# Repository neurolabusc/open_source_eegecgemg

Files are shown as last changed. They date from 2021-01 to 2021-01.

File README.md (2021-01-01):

# DIY Electrophysiology

**Note: this is an old page in an active field. Please see the links at
the bottom of the page for projects that extend this work.** Electrodes
on the skin can be used to measure muscle (electromyography, EMG) brain
(electroencephalography, EEG) and heart (electrocardiogram, ECG/EKG)
activity. These electrophysiological measures are popular for clinical,
research and hobbyist applications (such as brain computer interfaces).
Most commercial systems are "medical grade" -- these expensive systems
offer high precision (16-24 bits), participant electrical isolation as
well as support. On the other hand, there are numerous "hobby grade"
solutions that are very inexpensive but do provide fewer features. Here
we describe a "research grade" solution offering the same precision and
safety of the medical systems, with the ability to add time stamps (for
averaging data across trials) at a much lower cost (though without the
FDA approval or support, so use these designs at your own risk).

## Overview

This is an open source project for recording high quality
electrophysiological data using an ADS129n compatible front-end. These
chips support 4 (ADS1294), 6 (ADS1296) and 8 (ADS1298, ADS1299) channels
for measurement with 24-bit precision (and if you need even more
channels, you can daisy-chain multiple chips). The ADS communicates
using a serial peripheral interface (SPI) link. In this design, an
Arduino-compatible microcontroller translates between SPI and a
Bluetooth or USB Serial Port Connection. Software in the Matlab and
Processing languages allows a computer to record these serial port
signals. The connection between the computer and the Arduino should be
electrically isolated -- either via a wireless bluetooth module (the
JY-MCU sells for \$8) or an electrically isolated USB connection (e.g.
using an ADUM4160, \$11).

One nice feature of the ADS129n is that they provide 24-bit precision.
This allows a single hardware design to be used for very different
applications (spanning EEG to ECG and EMG). In contrast, a 16-bit design
needs to be tuned for the small and slow signals of scalp recorded EEG
or the quick and relatively huge signals generated by superficial
muscles in EMG. The chip also contains a number of sophisticated options
for filtering data and acquiring ECG. The newer ADS1299 is
pin-compatible with the ADS1298 providing a bit better precision but
requiring more current.

The host computer can send signals to control the amplifier (e.g.
specify the number of channels to send, the amplifier gain, sample rate,
etc). The software and datasheets describe how to do this. Once the
computer has specified the desired settings, a RDATAC (read data
continuously) causes the amplifier to begin streaming data back until a
SDATAC (stop continuous data) command is sent. In my code, the Arduino
converts serial port signals directly to SPI signals, so the host
software has complete control of the ads129n setup, and the code is
identical for SPI or serial port communication. However, my Arduino code
does alter the format for RDATAC data when transferring data from the
SPI to serial port. The reason for this is that the SPI interface has a
tremendous amount of bandwidth (e.g. the Teensy 3 can in theory support
21 Mbs), whereas Bluetooth connections are much more limited (e.g.
inexpensive Bluetooth modules max out at about .4 Mbs). For every
sample, the ADS129x SPI link will send 3+3\*n bytes of data per channel,
where n is 4 (ADS1294), 6 (ADS1296) and 8 (ADS1298, ADS1299). Therefore,
even when you record a single channel (3 bytes), the ADS1298 sends 27
bytes of data per sample. To conserve bandwidth, this project sends
1+3\*n where n is the number of ACTIVE channels. Therefore, if you set a
channel to be disabled ("input shorted") it will not require bandwidth.
The first sample transmitted via the serial port is the same header byte
reported by the SPI data format -- this includes a signature (to help
detect the first byte in each sample) and 4 bits that report the status
of the 4 GPIO (general purpose inputs/outputs) that allow you to record
time stamps. This sounds complicated, but the example Matlab and
Processing software demonstrate how to implement these communications.

## Implementation

I prefer to use a [Teensy 3.0
(T3)](https://www.pjrc.com/store/teensy3.html) for this application. It
is inexpensive, natively supports 3.3v signals, and can support high
speed (460800 bps in my experience) BlueTooth communications. The T3 has
a hardware SPI port (pins 10-13) and an additional hardware serial port
(pins 0 and 1) which can be used for a bluetooth module. The image shows
the connections. Pins 0 and 1 are connected to the Bluetooth module. Pin
4 is connected to the ADS "START". Pin 5 is connected to the ADS "DRDY"
(data ready). Pin 10 is connected to CS (Chip Select). Pin 10 (DOUT) is
connected to the ADS "DIN" (Data In) while Pin 11 (DIN) is connected to
the ADS "DOUT" (Data out). Pin 13 is connected to the ADS "CLK" (clock).
Optionally, connect pin 2 to PWDN (power down), pin 3 to RESET (reset)
and pin 6 to CLKSEL (clock source). To omit these connections, PWDN,
RESET and CLKSEL should in theory be pulled high (to 3.3v, DVDD), though
with the demonstration boards they float high so can be left
unconnected. Note you can always send the RESET command as an op-code
from software. The T3 will also supply power to ads129n front end board
-- you will want to provide 5v, 3.3v and 0v (ground) in addition to
linking the ads129n analog ground (AGND) to the T3 0v with a 0 Ohm 1/10
Watt resistor (which acts like a fuse to protect the participant). The
Due image below shows the location of these pins on the ads129n front
end boards. This code works with an Arduino Due as well, though in my
experience the BlueTooth modules are limited to around 115200 bps
speeds, so it is less well suited for wireless communication. However,
it is important to note that the upcoming [EEG
Mouse](https://github.com/OpenElectronicsLab/eeg-mouse) design will have
the same microprocessor as the Due, so software should be optimal for
that application. The essential wiring for connecting a Due to the
ads1298 or ads1299 front end kits is shown on the left. Note that this
figure shows the BOTTOM of the front end board (so that the header pins
are accessible) and the top of the Due (so its pins are also
accessible). The J4 jumper gets the 5v, 3.3v and 0v (ground) power. The
J3 jumper has the signal pins -- the required pins are pins are the SPI
clock (SCK), Data Out (DOUT), Data In (DIN), chip select (CS), Data
Ready (DRDY) and Start (START). Again, note that the Arduino and ads129n
cross their DIN/DOUT -- in the figure I use '->DIN' to show that this
Due (DOUT) pin connects to the ads129n DIN pin. You must also connect
the ground to of the Due to the analog ground of the ads129n -- this
should be done with a zero ohm 1/10 watt resistor (that acts as a fuse
for protecting the participant). The diagram also shows the pins for
connecting a blue tooth module (TX1, RX1) -- remember the bluetooth
module also requires power. Please note that for wired communications my
software assumes you will connect your Due to your computer's USB port
with the Due's fast "Native" port rather than the slow "Programmer" port
(the Due has two USB sockets). In theory, you could use other Arduino
compatible devices for connecting to the ads129n devices. However, the
Arduino would need to support SPI and would need to have a high speed
serial port (older designs like the Uno have very slow serial
connections). Two possible candidates are the Teensy 2.0 and Arduino
Leonardo. However, be warned that these devices use 5 volt signals that
may not work with and **could even damage the ads129n** (which can only
handle signals up to \~3.4 volts). Therefore, you would need to add
voltage dividers to each signal line. Therefore, the T3 and Due (that
natively operate at 3.3v) are simpler for this application, and
generally provide better performance.

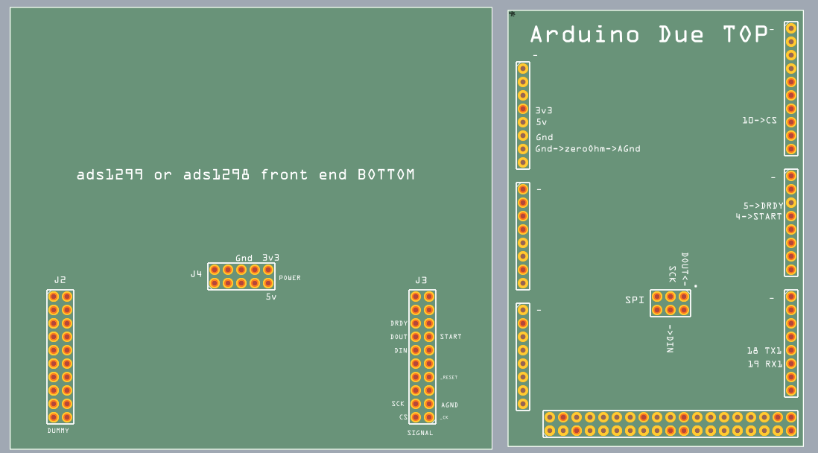
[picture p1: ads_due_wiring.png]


You can purchase the [ADS1298](https://www.ti.com/tool/ADS1298ECGFE-PDK)
(ideal for ECG) or [ADS1299](https://www.ti.com/tool/ads1299eegfe-pdk)
(ideal for EEG) Performance Demonstration Kits for about \$200. The
ADS1298 kit can connect to a standard EMG connector (about \$40). For
EMG or EEG you will probably be better served with the ADS1299 kit
connected to some DIN 42-802 sockets. In the near future expect to see a
less expensive, smaller open source design that can be used instead of
the demonstration kit (e.g. the [EEG Mouse
team's](https://github.com/OpenElectronicsLab/eeg-mouse) REV1 board will
integrate an Arduino compatible microcontroller on the same board as an
ADS1299, the previous REV0 design can be
[fabricated](https://oshpark.com/) and used instead of the demonstration
kit).

## Testing your wiring

The first program to run on your Arduino/T3 is the "adsArd_hello_world"
- this just makes sure that your Arduino is wired correctly to your
ads129n. Load this software onto your Arduino/T3 using a USB cable (make
sure to connect the cable to the 'Native' rather than 'Programmer' port
if you use a Due) and then select Tools/SerialMonitor. You should see a
message like "Device Type (ID Control Register): 62 Channels: 8"
repeated regularly. If this works, you have wired everything correctly.
If you are told the "Channels: 0" then there is a problem.

## Upgrading a Bluetooth Module

Most commercial Bluetooth modules are initially programmed to only
communicate at 9600bps. The included Arduino sketch
"Bluetooth_Programmer_Ard" allows you to reset your module for higher
speeds -- in my experience inexpensive modules run at 460800bps with the
Teensy 3 (and 115200 bps with the Due). You only have to run this script
once -- check the Arduino Serial Monitor to follow the progress. Once
your module is reprogrammed it will use the new speed whenever it is
restarted. Once you have reprogrammed your module, remember to put a
more useful sketch onto your Arduino (for example, the adsArd sketch
described below).

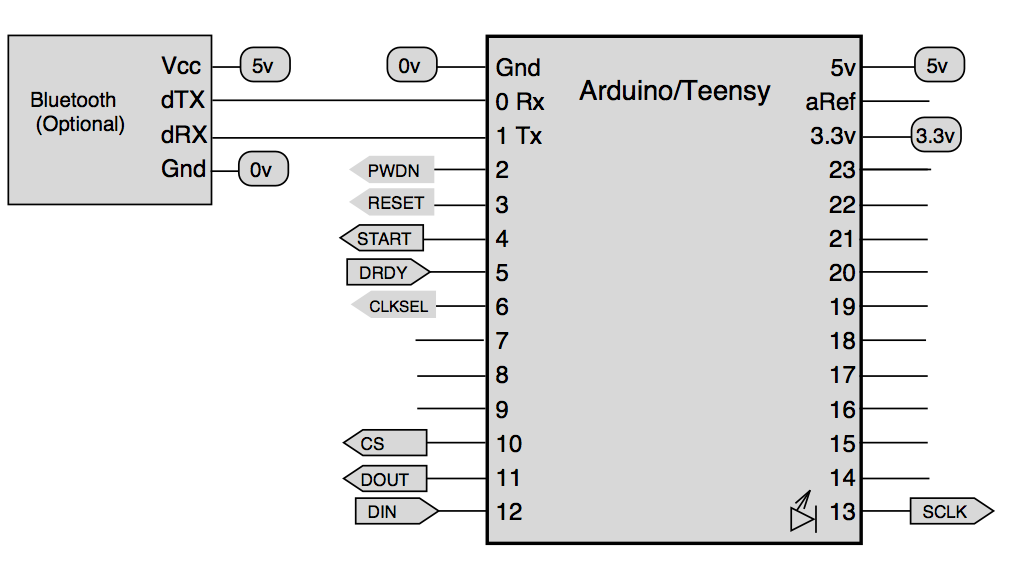
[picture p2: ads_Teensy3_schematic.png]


## Arduino Software

The Arduino sketch "adsArd" programs an Arduino-compatible device to
translate the ADS129n SPI data to the USB and BlueTooth ports. This
script has only been tested on the Teensy 3. We suspect it will work on
the Arduino Due once the developers tune the native serial port for
binary communications. Unless you use a Teensy3, you will need to edit a
few lines in adsCMD to specify the pins used for SPI communication (for
example, the [Teensy 2 uses pins 1,2,3 for SPI
communications](https://www.pjrc.com/teensy/td_libs_SPI.html) ). Once
your Arduino has been re-programmed, it will act as a SPI-serial
interposer whenever it is restarted. For the Teensy 3, the light on the
device will be off when the ADS129n is resting, dimly lit when the
ADS129n is streaming data, and will blink slowly if the Teensy is unable
to detect a ADS129x (check the connections between the Teensy and the
ADS129x).

## Matlab software

The Matlab software lets the user specify the sampling rate, number of
channels, and whether or not you wish to save the data. If requested,
the data will be saved in BrainVision analyzer format, which you can
view with the free ELEcro or EEGlab software.

## Processing software

By editing the first few lines of the Processing script you can specify
the sampling rate, number of channels, and whether or not you wish to
save the data. If requested, the data will be saved as tab-delimited
text. You can view these files with your favorite spreadsheet.

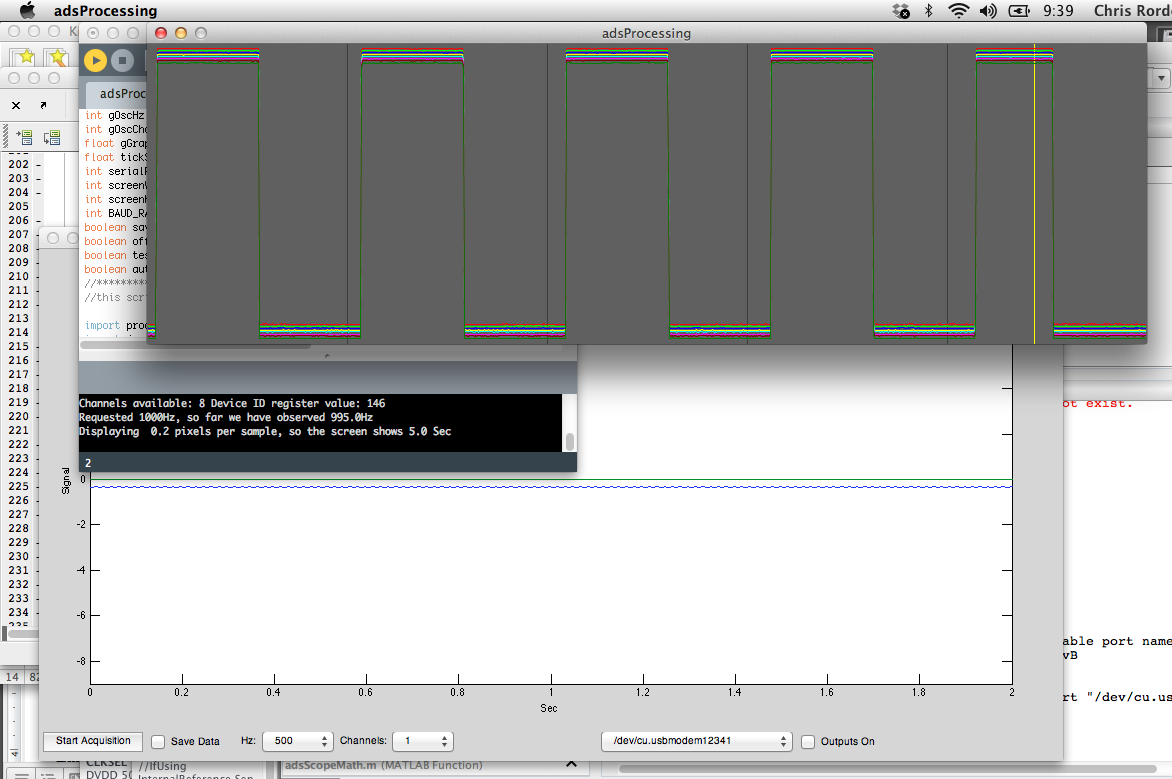
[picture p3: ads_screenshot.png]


## Links

 - [Chipstein](https://sites.google.com/site/chipstein/) describes probably the best hobby grade EMG (16-bit) and EEG (10-bit) around. The section on electrodes and skin preparation is vital for any electrophysiological recording.
 - The [EEG Mouse](https://github.com/OpenElectronicsLab/eeg-mouse) team are developing a complete open source ADS129n hardware project with an Arduino-compatible processor built onto the board. Our intention is that the software we describe on this page can be used on this hardware to record data.
 - The [ADS1298ECG Front End Performance Demonstration Kit](https://www.ti.com/tool/ADS1298ECGFE-PDK) includes a ADS1298 module that can be directly plugged into a Teensy 3 or other Arduino compatible device. Note that the configuration of the input channels is really optimized for ECG rather than EMG or EEG. The ads129n can do some sophisticated preprocessing of ECG data. EMG and EEG are simpler, but if you wish to use this demonstration kit for those applications you will need to use the jumpers appropriately.
 - [Raul Aguaviva](https://codinglab.blogspot.be/2013/07/my-heartbeat.html) describes a simple ECG system that can input into his [XOscillo](https://code.google.com/archive/p/xoscillo/) software.
 - [Scott Harden](https://www.swharden.com/blog/2013-04-14-simple-diy-ecg-pulse-oximeter-version-2/) describes the an elegantly simple hobby-grade ECG and optical pulse measurement system.
 - [Josh Wojnas](https://sites.google.com/site/openloopproject/Home/code-valt) provides plans for a simple ADS1298 hardware board.
 - StarCat provides the [HackEEG shield](https://starcat.io/products/hackeeg-shield/)
 - [OpenBCI](https://shop.openbci.com) provides impressive products.
 - The work described here has been extended by [Adam Feuer](https://github.com/adamfeuer/ADS129x-tools).

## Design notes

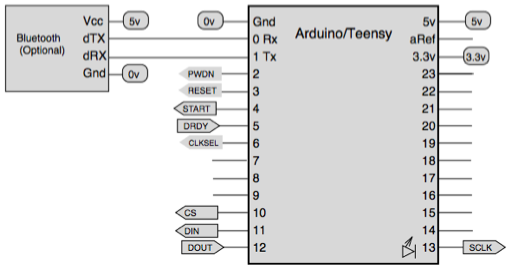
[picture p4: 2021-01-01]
source/teensy_wiring/ads_schematic.sketch/QuickLook/Thumbnail.png

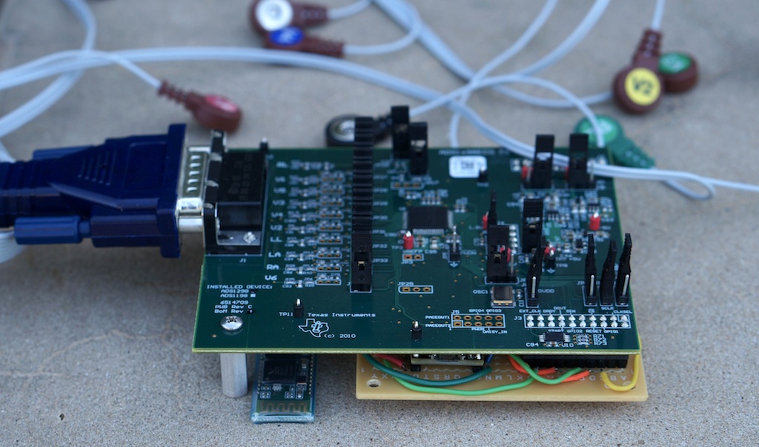
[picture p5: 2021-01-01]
photo_small.jpg

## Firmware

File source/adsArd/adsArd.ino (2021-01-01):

#define BAUD_RATE  460800 //specifies BlueTooth speed. top speeds appear to be around 115200 for Due, 460800 for Teensy3
#define txActiveChannelsOnly //reduce bandwidth: only send data for active data channels

#if defined(__SAM3X8E__)
  #define isDUE  //Detect Arduino Due
  #define WiredSerial SerialUSB //use Due's Native port
#else  
  #define WiredSerial Serial
#endif

#include "ads1298.h"
#include "adsCMD.h"
#include <SPI.h>  // include the SPI library:
int gMaxChan = 0;
int gNumActiveChan = 0;
int activeSerialPort = 0; //data will be sent to serial port that last sent commands. E.G. bluetooth or USB port
boolean gActiveChan [9]; // reports whether channels 1..9 are active
const int kPIN_LED = 13;//pin with light - typically 13. Only flashes if error status. n.b. on Teensy3, pin 13 is ALSO spi clock!
boolean isRDATAC = false;


void detectActiveChannels() {  //set device into RDATAC mode -it will stream data
  if ((isRDATAC) ||  (gMaxChan < 1)) return; //we can not read registers when in RDATAC mode
  using namespace ADS1298; 
  gNumActiveChan = 0;
  for (int i = 1; i <= gMaxChan; i++) {
    delayMicroseconds(1); 
     int chSet = adc_rreg(CHnSET + i);
     gActiveChan[i] = ((chSet & 7) != SHORTED);
     if ( (chSet & 7) != SHORTED) gNumActiveChan ++;   
  }
}

int Serialavailable(int serialNum) { //handle commands to ADS device
  switch (serialNum) {
    case 1:
      return Serial1.available() ;
    default: 
      return WiredSerial.available() ;
  }
}

int Serialread(int serialNum) { //handle commands to ADS device
  switch (serialNum) {
    case 1:
      return Serial1.read() ;
    default: 
      return WiredSerial.read() ;
  }
}

void checkSerialNum(int serialNum) { //handle commands to ADS device
  if (Serialavailable(serialNum) < 1) return;
  activeSerialPort = serialNum;
  unsigned char  val = Serialread(serialNum);      
  using namespace ADS1298; 
  if ((val >= 0x02) && (val <= 0x12)) { //single byte command
        if (val == RDATAC) {
          detectActiveChannels(); //start streaming data
          if (gNumActiveChan > 0) isRDATAC = true;
        }
        if (val == SDATAC) isRDATAC = false;
        if (val == RDATA) isRDATAC = false;
        adc_send_command(val);
        return;
  }
  if ((val >= 0x20) && (val <= 0x3F)) { //RREG (Read register) command  
      for (int i = 0; i < 10; ++i) if (Serialavailable(serialNum) < 1) delay(1); 
      if(Serialavailable(serialNum) < 1) return;
      unsigned char  numSerialBytes = Serialread(serialNum)+1;
      digitalWrite(IPIN_CS, LOW);
      SPI.transfer(val);
      SPI.transfer(numSerialBytes-1);	// number of registers to be read – 1
      unsigned char serialBytes[numSerialBytes];
      for (int i = 0; i < numSerialBytes; ++i) 
        serialBytes[i] =SPI.transfer(0);
      delayMicroseconds(1);     
      digitalWrite(IPIN_CS, HIGH);
      switch (serialNum) {
        case 1:
          Serial1.write(serialBytes, numSerialBytes);
          Serial1.flush();
          break;
        default: 
            WiredSerial.write(serialBytes, numSerialBytes);
            WiredSerial.flush();
      }
      return;
  }
  if ((val >= 0x40) && (val <= 0x5F)) { //WREG (Write Register) command
      for (int i = 0; i < 5; ++i) if (Serialavailable(serialNum) < 1) delay(1); 
      if(Serialavailable(serialNum) < 1) return;
      unsigned char  numSerialBytes = Serialread(serialNum)+1;
      for (int i = 0; i < 5; ++i) if (Serialavailable(serialNum) < numSerialBytes) delay(1); 
      if(Serialavailable(serialNum) < numSerialBytes) return;
      unsigned char serialBytes[numSerialBytes];
      for (int i = 0; i < numSerialBytes; ++i) serialBytes[i] = Serialread(serialNum); 
      digitalWrite(IPIN_CS, LOW);
      SPI.transfer(val);
      SPI.transfer(numSerialBytes-1);	// number of registers to be written – 1
      for (int i = 0; i < numSerialBytes; ++i) {
        SPI.transfer(serialBytes[i]);
        delayMicroseconds(1);      
      }
      digitalWrite(IPIN_CS, HIGH);
  }//if WREG
}

//#define testSignal //use this to determine if your software is accurately measuring full range 24-bit signed data -8388608..8388607
#ifdef testSignal
  int testInc = 1;
  int testPeriod = 100;
  byte testMSB, testLSB; 
#endif 

void sendOsc(void) { 
    if ((!isRDATAC) || (gNumActiveChan < 1) )  return;
    if (digitalRead(IPIN_DRDY) == HIGH) return; 
    digitalWrite(IPIN_CS, LOW);
    #ifdef txActiveChannelsOnly
      int numSerialBytes = 1 + (3 * gNumActiveChan); //8-bits header plus 24-bits per ACTIVE channel
      unsigned char serialBytes[numSerialBytes];
      int i = 0;
      serialBytes[i++] =SPI.transfer(0); //get 1st byte of header
      SPI.transfer(0); //skip 2nd byte of header
      SPI.transfer(0); //skip 3rd byte of header
      for (int ch = 1; ch <= gMaxChan; ch++) {
        if (gActiveChan[ch]) {
           #ifdef testSignal
            //positive full-scale input produces  7FFFFFh, negative full-scale input produces 800000h, neutroal produces 000000h 
            testInc++;
            if (testInc >= testPeriod) {
              testInc = 1;
              if (testMSB == 0x7F) { //send minimum value -8388608;
                testMSB = 0x80;
                testLSB = 0x00;
              } else if (testMSB == 0x80) { //send zero
                testMSB = 0x00;
                testLSB = 0x00;             
              } else { //send maximum value +8388607
                testMSB = 0x7F;
                testLSB = 0xFF;
              } 
            }
            serialBytes[i++] = testMSB;
            serialBytes[i++] = testLSB;
            serialBytes[i++] = testLSB;
            SPI.transfer(0); SPI.transfer(0); SPI.transfer(0);
          #else //if testSignal otherwise report real data
            serialBytes[i++] =SPI.transfer(0);
            serialBytes[i++] =SPI.transfer(0);
            serialBytes[i++] =SPI.transfer(0); 
          #endif
        } else {
          SPI.transfer(0); SPI.transfer(0); SPI.transfer(0); //skip these 24 bytes
        }  
      }
      //for (int i = 0; i < numSerialBytes; ++i) 
      //  serialBytes[i] =SPI.transfer(0);
    #else
      int numSerialBytes = (3 * (gMaxChan+1)); //24-bits header plus 24-bits per channel
      unsigned char serialBytes[numSerialBytes];
      for (int i = 0; i < numSerialBytes; ++i) 
        serialBytes[i] =SPI.transfer(0);
     #endif 
     delayMicroseconds(1); 
     digitalWrite(IPIN_CS, HIGH);
     switch (activeSerialPort) {
        case 1:
          Serial1.write(serialBytes, numSerialBytes);
          break;
        default: 
            WiredSerial.write(serialBytes, numSerialBytes);;
      }
}

void adsSetup() { //default settings for ADS1298 and compatible chips
        using namespace ADS1298;
        // All GPIO set to output 0x0000: (floating CMOS inputs can flicker on and off, creating noise)
	adc_wreg(GPIO, 0);
        adc_wreg(CONFIG3,PD_REFBUF | CONFIG3_const);
	//FOR RLD: Power up the internal reference and wait for it to settle
        // adc_wreg(CONFIG3, RLDREF_INT | PD_RLD | PD_REFBUF | VREF_4V | CONFIG3_const);
	// delay(150);
	// adc_wreg(RLD_SENSP, 0x01);	// only use channel IN1P and IN1N
	// adc_wreg(RLD_SENSN, 0x01);	// for the RLD Measurement
        adc_wreg(CONFIG1,HIGH_RES_1k_SPS);
        adc_wreg(CONFIG2, INT_TEST);	// generate internal test signals
	// Set the first two channels to input signal
	for (int i = 1; i <= 8; ++i) {
		adc_wreg(CHnSET + i, ELECTRODE_INPUT | GAIN_12X); //report this channel with x12 gain
		//adc_wreg(CHnSET + i, TEST_SIGNAL | GAIN_12X); //create square wave
                //adc_wreg(CHnSET + i,SHORTED); //disable this channel
	}
	digitalWrite(PIN_START, HIGH);  
}

void setup(){
  using namespace ADS1298;
  //prepare pins to be outputs or inputs
  //pinMode(PIN_SCLK, OUTPUT); //optional - SPI library will do this for us
  //pinMode(PIN_DIN, OUTPUT); //optional - SPI library will do this for us
  //pinMode(PIN_DOUT, INPUT); //optional - SPI library will do this for us
  pinMode(IPIN_CS, OUTPUT);
  pinMode(PIN_START, OUTPUT);
  pinMode(IPIN_DRDY, INPUT);
  //pinMode(PIN_CLKSEL, OUTPUT);//*optional
  //pinMode(IPIN_RESET, OUTPUT);//*optional
  //pinMode(IPIN_PWDN, OUTPUT);//*optional
  //start small peripheral interface
  SPI.begin();
  SPI.setBitOrder(MSBFIRST);
  #ifndef isDUE
  SPI.setClockDivider(SPI_CLOCK_DIV4); //http://forum.pjrc.com/threads/1156-Teensy-3-SPI-Basic-Clock-Questions
  #endif
  SPI.setDataMode(SPI_MODE1);
  //Start ADS1298
  delay(500); //wait for the ads129n to be ready - it can take a while to charge caps
  //digitalWrite(PIN_CLKSEL, HIGH);//*optional
  //delay(1);digitalWrite(IPIN_PWDN, HIGH);//*optional - turn off power down mode
  //digitalWrite(IPIN_RESET, HIGH);delay(100);//*optional
  //digitalWrite(IPIN_RESET, LOW);delay(1);//*optional
  //digitalWrite(IPIN_RESET, HIGH);delay(1);  //*optional Wait for 18 tCLKs AKA 9 microseconds, we use 1 millisec
  // Send SDATAC Command (Stop Read Data Continuously mode)
  delay(100); //pause to provide ads129n enough time to boot up...
  adc_send_command(SDATAC);
  delay(10);
  // Determine model number and number of channels available
  int IDval = adc_rreg(ID) ; 
  switch (IDval & B00011111 ) { //least significant bits reports channels
          case  B10000: //16
            gMaxChan = 4; //ads1294
            break;
          case B10001: //17
            gMaxChan = 6; //ads1296
            break; 
          case B10010: //18
            gMaxChan = 8; //ads1298
            break;
          case B11110: //30
            gMaxChan = 8; //ads1299
            break;
          default: 
            gMaxChan = 0;
  }
  //start serial port
  Serial1.begin(BAUD_RATE);
  Serial1.flush(); //flush all previous received and transmitted data
  WiredSerial.begin(9600); //use native port on Due
  while (WiredSerial.read() >= 0) {} //http://forum.arduino.cc/index.php?topic=134847.0
  delay(200);  // Catch Due reset problem
  //while (!WiredSerial) ; //required by Leonardo http://arduino.cc/en/Serial/IfSerial (ads129n requires 3.3v signals, Leonardo is 5v)
  if (gMaxChan == 0) { //error mode
    pinMode(kPIN_LED, OUTPUT);
    while(1) { //loop forever 
      digitalWrite(kPIN_LED, HIGH);   // turn the LED on (HIGH is the voltage level)
      delay(500);               // wait for a second
      digitalWrite(kPIN_LED, LOW);    // turn the LED off by making the voltage LOW
      delay(500); 
    } //while forever
  } //error mode
  adsSetup(); //optional - sets up device - the PC can do this as well       
} //setup()

void loop()
{
    //checkSerial(); //see if there are any new commands
    checkSerialNum(1); //wireless
    checkSerialNum(0); //wired
    sendOsc(); //see if there are any new samples to report
} //loop()
